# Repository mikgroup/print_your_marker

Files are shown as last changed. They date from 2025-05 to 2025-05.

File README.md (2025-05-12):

# How to Print Your Marker: an Open-Source, Easy-to-Make, Compact Active Wireless Marker for Motion Tracking

Released CAD for the wireless marker design presented at ISMRM 2025 (Abstract #4589):

A. De Goyeneche, J. Maravilla, K. Gopalan, A. Falk, S. Yu, C. Liu, M. Lustig. “How to Print Your Marker: an Open-Source, Easy-to-Make, Compact Active Wireless Marker for Motion Tracking”. *Proceedings of the 34th Annual Meeting of ISMRM, Honolulu, Hawaii, USA, 2025.* 

This repository provides an easy-to-assemble, compact, open-source 3D-printed marker housing for use in MRI applications.  
It is designed to support existing wireless RF marker circuits based on inductive coupling, and simplifies construction for broader use and reproducibility.

## Overview

Markers Overview

- Compact design (<11 × 7 × 6 mm).
- Two-part SLA-printed shell.
- Cavity for Gd-doped water signal source.
- Passive detuning using crossed diodes.
- Rapid localization using projection acquisitions.

### Bill of materials

- Enamel-insulated copper wire.
- SMD 1111 form factor capacitor (we used 39 pF to tune to ~127.7MHz).
- 2x MA4P7446F for crossed diodes.
- SLA 3D printer (we used clear resin).
- Gd-doped water solution (e.g. 10nM for ~5ms T1 and T2).
- UV glue or sealant.

### Assembly instructions 

Assembly Steps

1. **3D Print** the two-piece shell. 
1. **Coil the wire**: Loop the wire three times along the groove around the spherical cavity on the base piece. Expose the wire sections by the components compartment. Trim the wire ends to align with the end of the component-holding structure on each side.
1. **Assemble**: Place the capacitor on the base piece and the crossed diodes on the cap piece. 
1. **Close & Solder**: Fit the cap onto the base and obtain a tight fit with a vise or similar tool. Apply flux to the exposed wire and components and solder each side. Clear print resin is useful for observing the solder flow and ensuring a complete connection.
1. **Tune**: Using a Vector Network Analyzer (VNA), slightly adjust the spacing between coil turns to tune the marker to the desired frequency (e.g., looking for a dip in S11 at ~127.7 MHz).
1. **Fill & Seal**: Fill the cavity with Gd-doped water solution through the top hole and seal it (e.g., using UV-curable glue). Re-tune if necessary.

### Citation

If you use or adapt this design, please cite:

A. De Goyeneche et al., “How to Print Your Marker: an Open-Source, Easy-to-Make, Compact Active Wireless Marker for Motion Tracking.” ISMRM 2025, Abstract #4589.

### License

Licensed under CC BY-NC 4.0 — for non-commercial research use only.



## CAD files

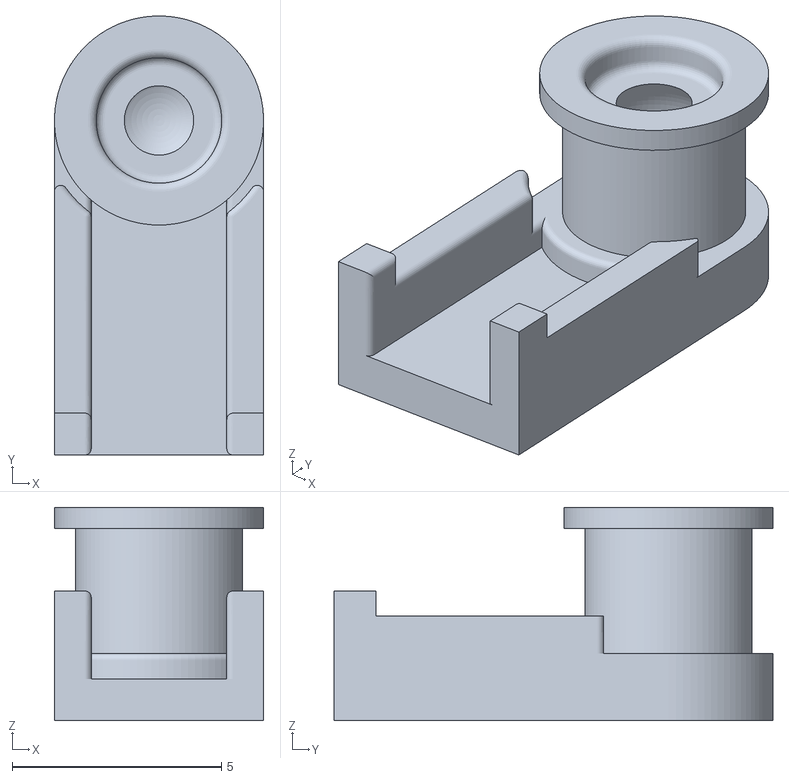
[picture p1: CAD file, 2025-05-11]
STL Files/Marker 3mm Sphere Base.stl
5.00 x 10.5 x 5.10

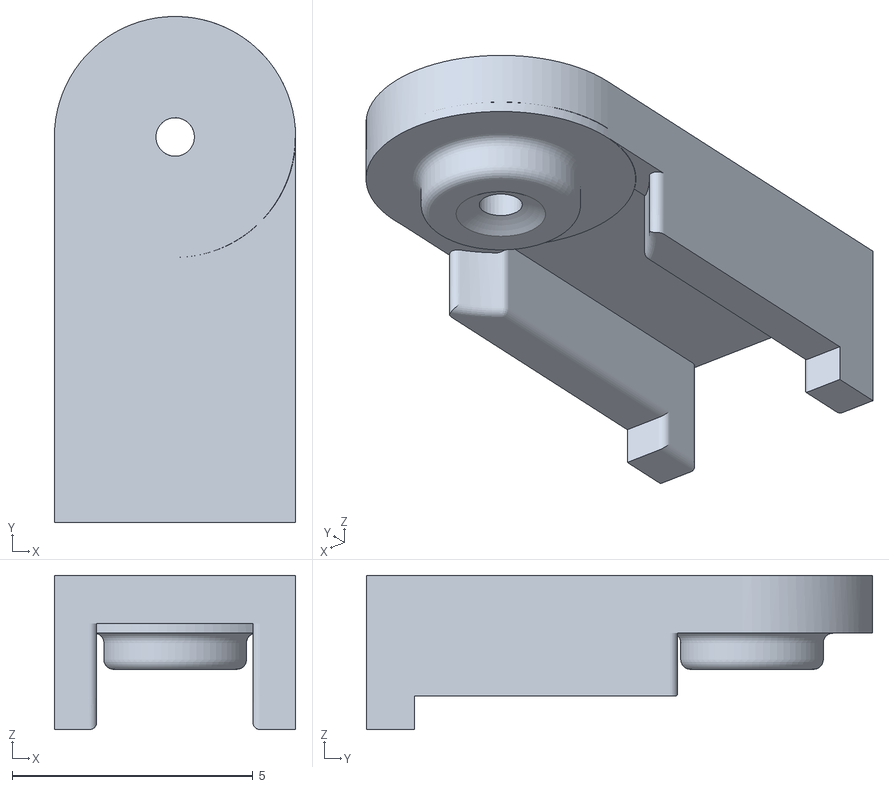
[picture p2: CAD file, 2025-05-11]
STL Files/Marker 3mm Sphere Cap.stl
5.01 x 10.5 x 3.20
